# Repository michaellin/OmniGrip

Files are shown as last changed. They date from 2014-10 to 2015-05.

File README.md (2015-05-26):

## Description
The OmniGrip is a master manipulator gripper device capable of rendering a programmed stiffness. This open source project aims to add a seventh degree of freedom to the conventional Sensable Touch (Phantom Omni) haptic device. The project's files can be found at our [github repository](https://github.com/michaellin/OmniGrip). There are two versions of the device. The RE model uses a [Maxon RE-25 Motor](http://www.engr.ucsb.edu/~mdnip/me170c/datasheets/25mm_Motors.pdf) and the A-Max model uses a [Maxon A-Max-22 Motor](http://www.farnell.com/datasheets/484760.pdf). NOTE: the software currently only supports the RE model. It has not been tested for the A-Max model yet. For more details about the device refer to the conference paper: <link to future paper>.

## Assembly Instructions
List of materials needed to assemble the OmniGrip:

(quantity) description [McMaster-Carr part number]

1. (8) 3D printed parts of the device
  1. Long lever
  2. Short lever
  3. Frame center piece
  4. Frame top piece
  5. Frame bottom piece
  6. Long capstan gear
  7. Short capstan gear
  8. Handle
2. (6) Mini High-Precision Ball Bearing - ABEC-5                                                                [MC 57155K355]
3. (1) 10 Ft. Type 304 Stainless Steel Wire Rope, 7x19 Strand Core, 0.024" Dia, 70 Lb Break Strength, 10' Long  [MC 3461T621]
4. (2) Vented 18-8 Ss Socket Head Cap Screw, 4-40 Thread, 1/2" Length, .035" Vent Diameter                      [MC 93235A110]
5. (8) Type 316 Ss Socket Head Cap Screw, 0-80 Thread, 1/4" Long                                                [MC 92185A053]
6. (8) Brass Press-Fit Expansion Insert for Plastics without Flange, 0-80 Internal Thread, 1/8" Length          [MC 92395A109]
7. (2) Type 316 Stainless Steel Socket Head Cap Screw, 2-56 Thread, 1/4" Length                                 [MC 92185A077]
8. (2) Brass Press-Fit Expansion Insert for Plastics without Flange, 2-56 Internal Thread, 5/32" Length         [MC 92395A111]
9. (3) Metric 316 Stainless Steel Pan Head Phillips Machine Screw, M2 Size, 5mm Length, .4mm Pitch              [MC 90116A009]
10. (2) Copper Oval Compression Sleeve for 1/32" Rope Diameter, 1/4" Sleeve Length                              [MC 3897T31]

Important Note: most McMaster-Carr parts come in packs. The number specified in the parenthesis is just the amount of units used, not the number of packs you need to buy.

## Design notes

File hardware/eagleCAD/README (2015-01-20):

When using EagleCAD to open the Prototype layouts, some references might be broken initially. Relocate the files in "./lib/SparkFun-*". (* means wildcard/anything)

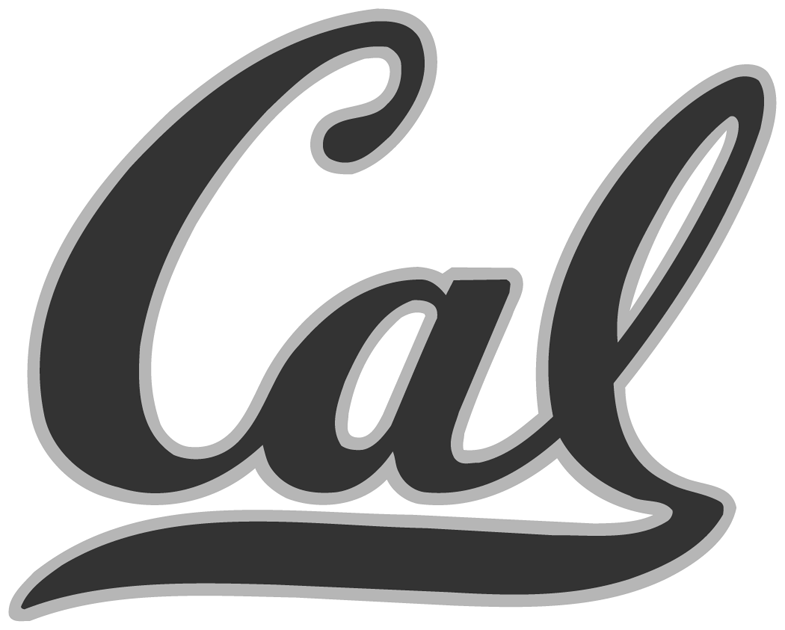
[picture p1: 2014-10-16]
hardware/eagleCAD/emblems/cal.bmp

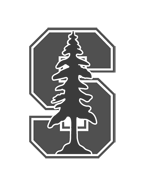
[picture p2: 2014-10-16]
hardware/eagleCAD/emblems/SU_BlockStree_2color copy.bmp

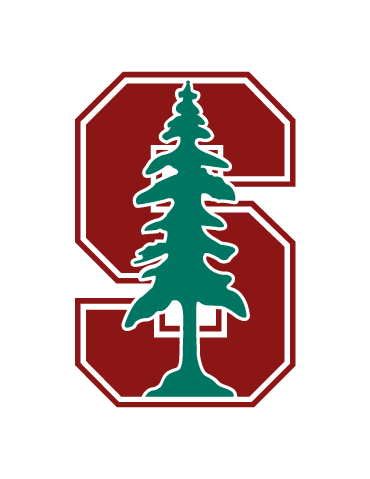
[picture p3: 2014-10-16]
hardware/eagleCAD/emblems/SU_BlockStree_2color.png

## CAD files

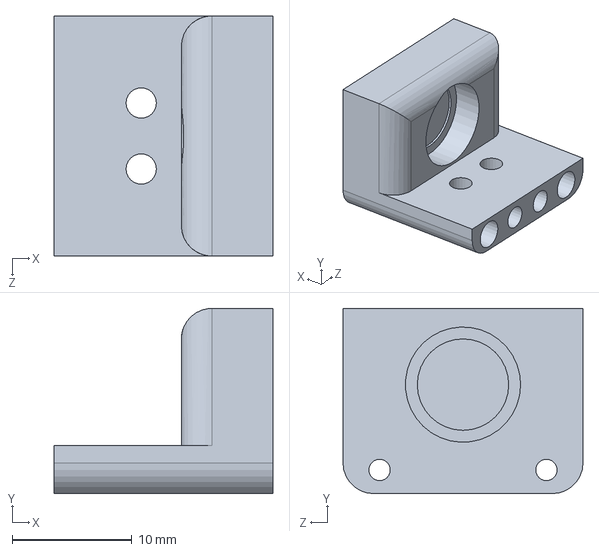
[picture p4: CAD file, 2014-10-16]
hardware/SolidWorksCAD/Model-AMAX-Motor/Center Piece RE 25.SLDPRT
18.2 x 15.4 x 20.0 mm

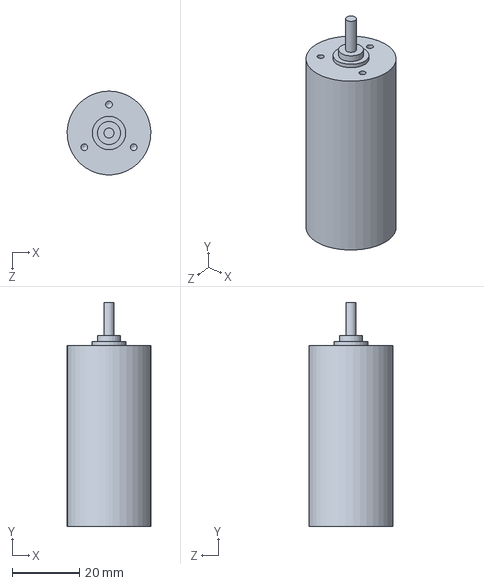
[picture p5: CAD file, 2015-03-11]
hardware/SolidWorksCAD/Model-RE-Motor/RE25 Motor.SLDPRT
25.0 x 66.8 x 25.0 mm

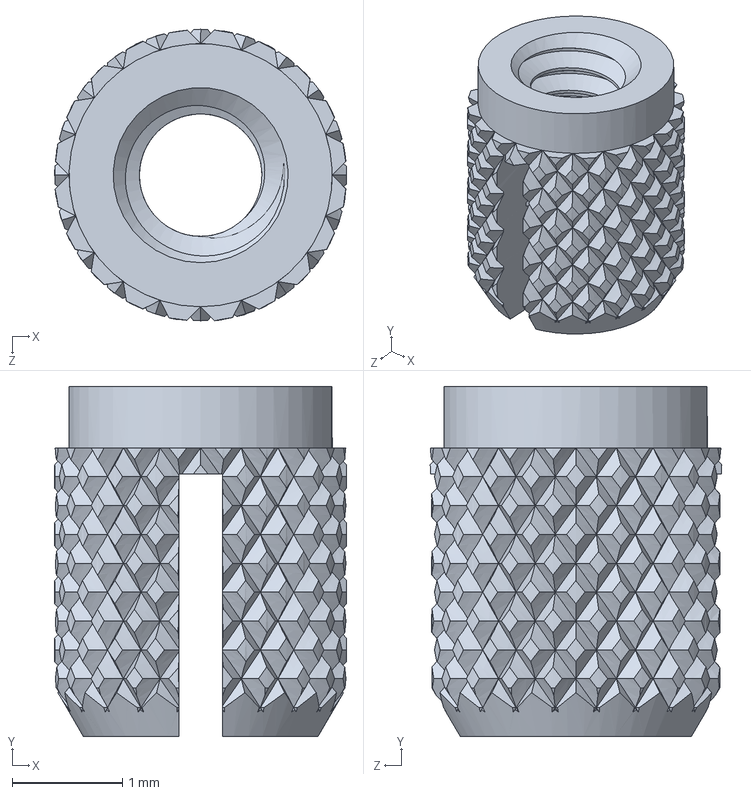
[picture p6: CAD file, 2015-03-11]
hardware/SolidWorksCAD/Model-RE-Motor/BrassInsert 0-80.SLDPRT
2.65 x 3.17 x 2.64 mm

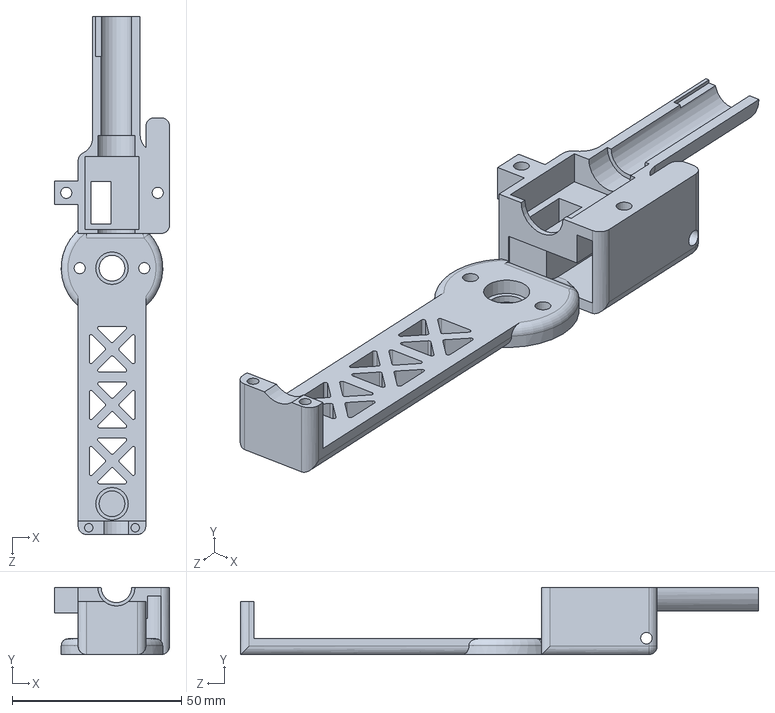
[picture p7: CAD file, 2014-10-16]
hardware/SolidWorksCAD/Model-AMAX-Motor/Top Piece Amax.SLDPRT
34.0 x 19.8 x 152.9 mm

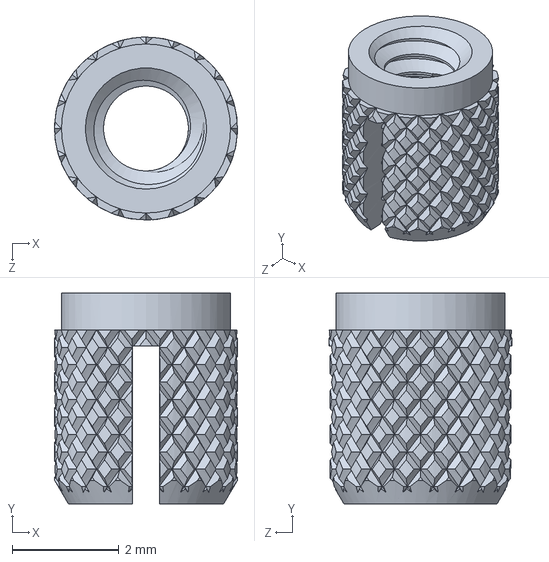
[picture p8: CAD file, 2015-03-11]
hardware/SolidWorksCAD/Model-RE-Motor/Brass Insert 2-56.SLDPRT
3.44 x 3.96 x 3.43 mm

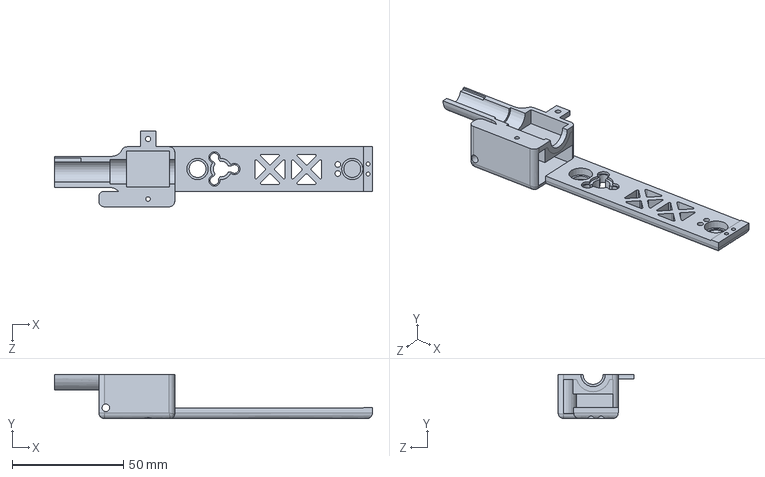
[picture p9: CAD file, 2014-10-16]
hardware/SolidWorksCAD/Model-AMAX-Motor/Bottom Piece Amax.SLDPRT
142.9 x 19.8 x 34.0 mm

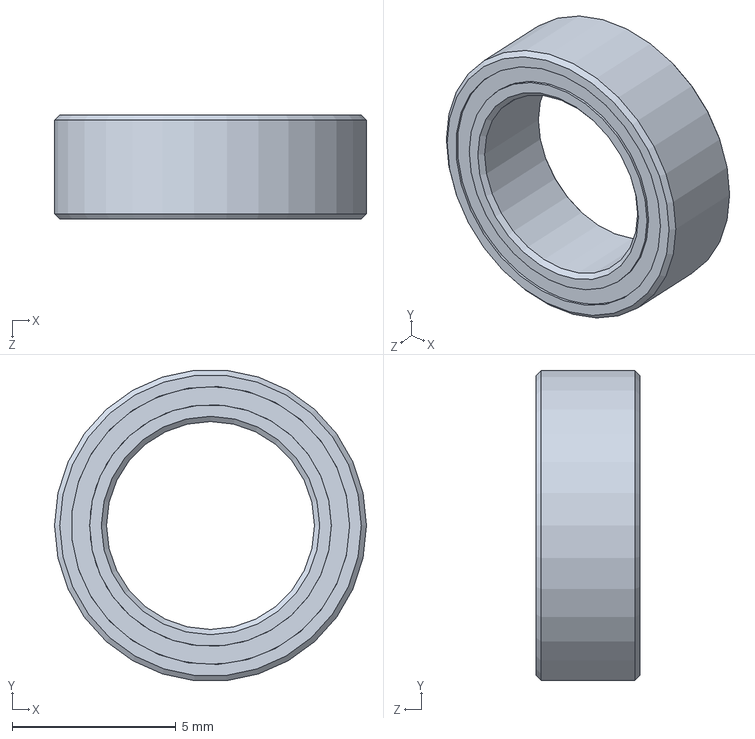
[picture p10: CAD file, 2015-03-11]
hardware/SolidWorksCAD/Model-RE-Motor/.25ID_.375OD_Bearing_60355K440.SLDPRT
9.53 x 9.47 x 3.17 mm

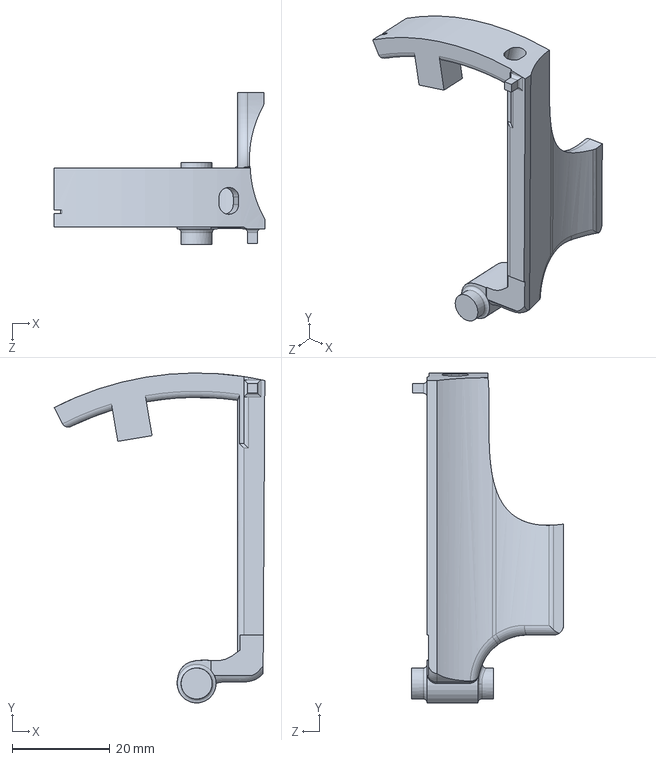
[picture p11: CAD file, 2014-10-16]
hardware/SolidWorksCAD/Model-AMAX-Motor/Long Lever Amax.SLDPRT
43.1 x 67.5 x 31.1 mm

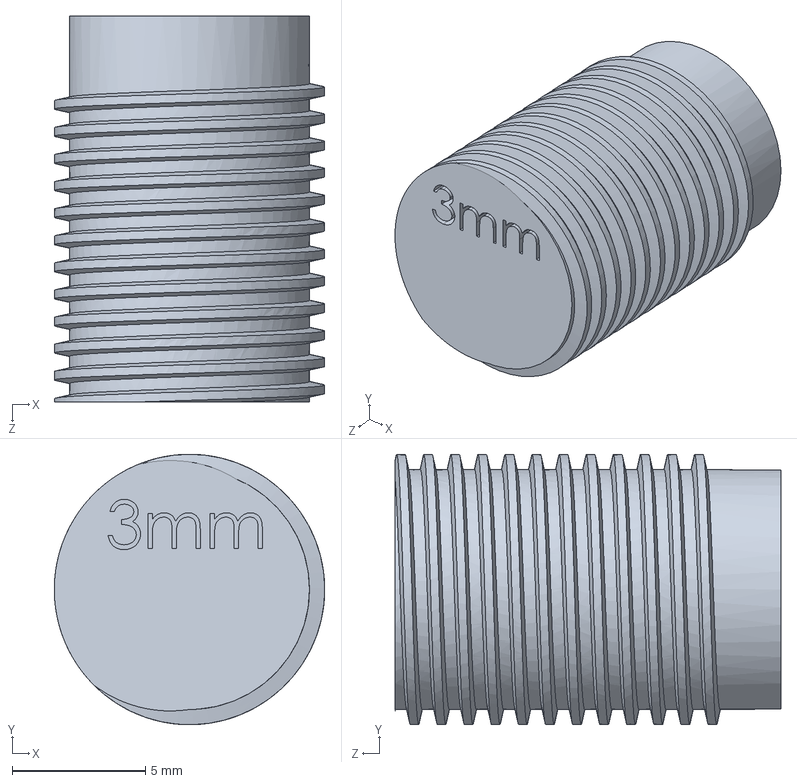
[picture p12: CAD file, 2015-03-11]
hardware/SolidWorksCAD/Model-RE-Motor/MIMA_capstan_h08in_d025in_3mm_RE 25.SLDPRT
10.1 x 10.1 x 14.5 mm

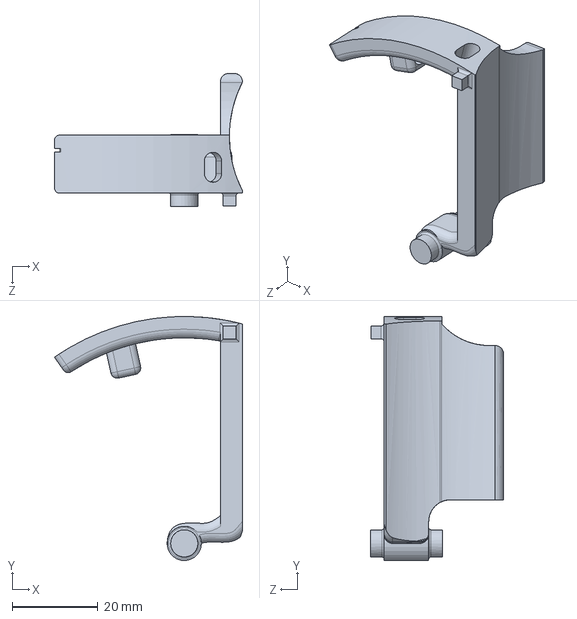
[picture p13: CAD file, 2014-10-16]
hardware/SolidWorksCAD/Model-AMAX-Motor/Short Lever Amax.SLDPRT
43.9 x 57.0 x 31.1 mm

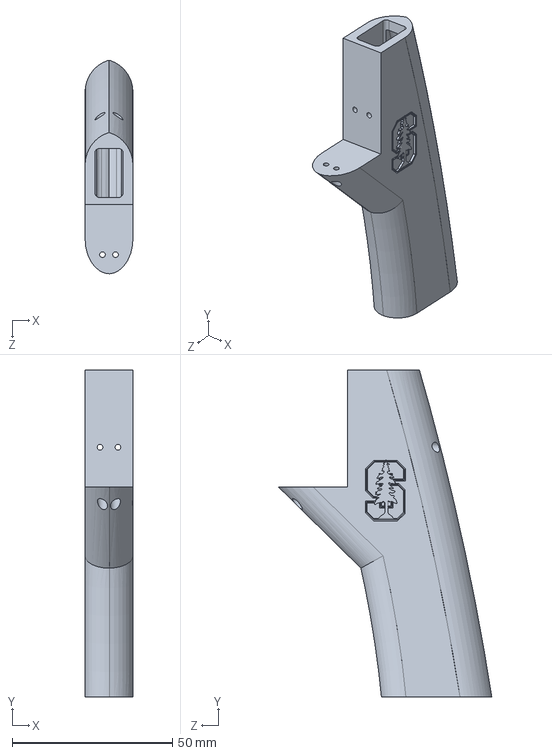
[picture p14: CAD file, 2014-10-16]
hardware/SolidWorksCAD/Model-AMAX-Motor/Handle Amax.SLDPRT
14.9 x 102.0 x 66.7 mm

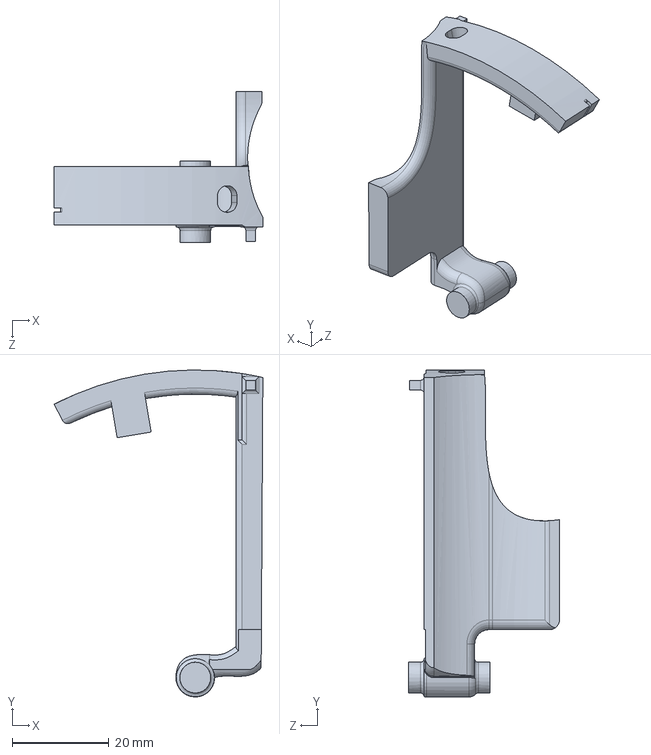
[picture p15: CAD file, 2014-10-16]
hardware/SolidWorksCAD/Model-RE-Motor/Long Lever RE 25.SLDPRT
43.1 x 67.5 x 31.1 mm

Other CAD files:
hardware/SolidWorksCAD/Model-AMAX-Motor/Center Piece Amax.SLDPRT
hardware/SolidWorksCAD/Model-RE-Motor/0-80_Brass Inserts_92395A109.SLDPRT
hardware/SolidWorksCAD/Model-RE-Motor/Top Piece RE 25.SLDPRT
hardware/SolidWorksCAD/Model-RE-Motor/Handle RE 25.SLDPRT
hardware/SolidWorksCAD/Model-RE-Motor/Bottom Piece RE 25.SLDPRT
hardware/SolidWorksCAD/Model-RE-Motor/Short Lever RE 25.SLDPRT
hardware/SolidWorksCAD/Model-RE-Motor/0-80 CapScrew .25''.SLDPRT
hardware/SolidWorksCAD/Model-RE-Motor/0-80_Socket_Cap_Screw_92200A055.SLDPRT
hardware/SolidWorksCAD/Model-RE-Motor/2-56 screw .25 length.SLDPRT
hardware/SolidWorksCAD/Model-RE-Motor/Bottom Piece RE 25.STL
hardware/SolidWorksCAD/Model-RE-Motor/M2 screw lg-5mm.SLDPRT
hardware/SolidWorksCAD/Model-RE-Motor/MIMA_capstan_h08in_d025in_Passive_Long.SLDPRT
hardware/SolidWorksCAD/Model-RE-Motor/Short Lever RE 25.STL

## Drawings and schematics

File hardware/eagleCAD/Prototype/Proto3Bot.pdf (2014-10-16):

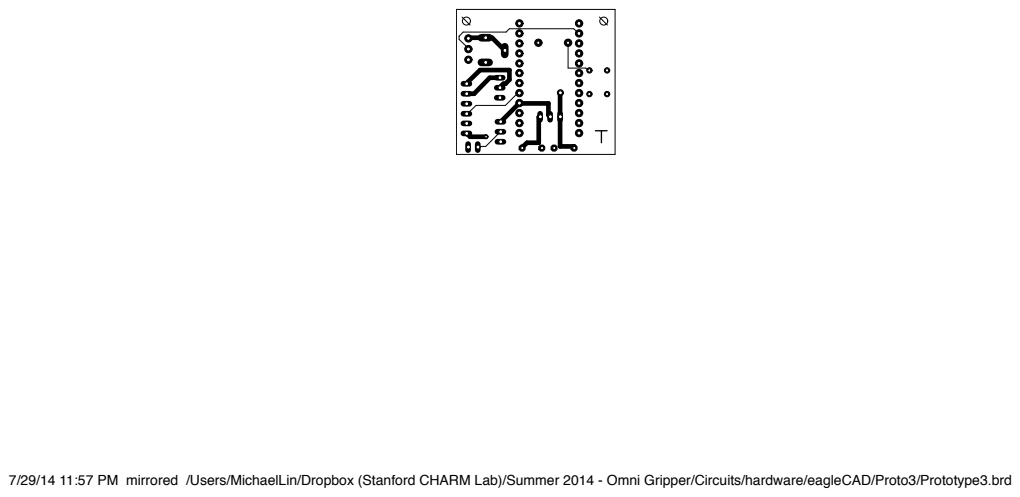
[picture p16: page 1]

7/29/14 11:57 PM mirrored /Users/MichaelLin/Dropbox (Stanford CHARM Lab)/Summer 2014 - Omni Gripper/Circuits/hardware/eagleCAD/Proto3/Prototype3.brd

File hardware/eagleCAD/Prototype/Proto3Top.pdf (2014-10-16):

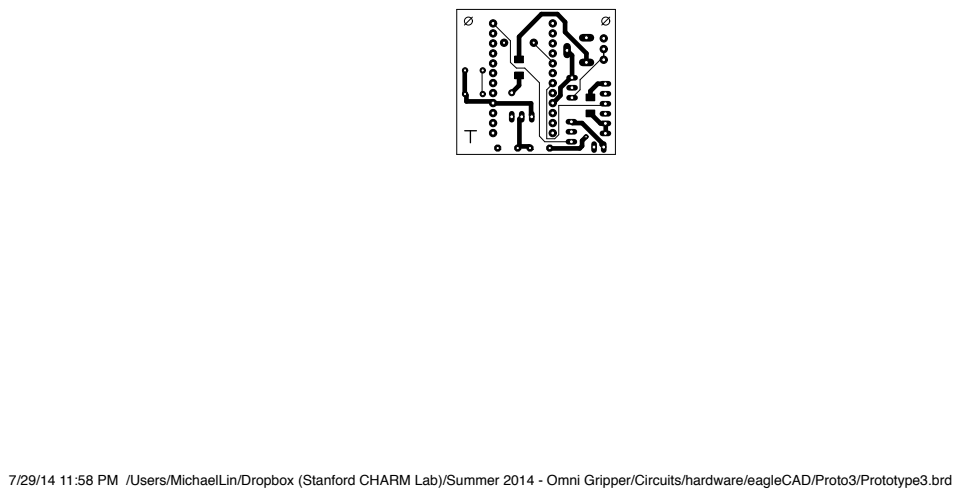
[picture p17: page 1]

7/29/14 11:58 PM /Users/MichaelLin/Dropbox (Stanford CHARM Lab)/Summer 2014 - Omni Gripper/Circuits/hardware/eagleCAD/Proto3/Prototype3.brd

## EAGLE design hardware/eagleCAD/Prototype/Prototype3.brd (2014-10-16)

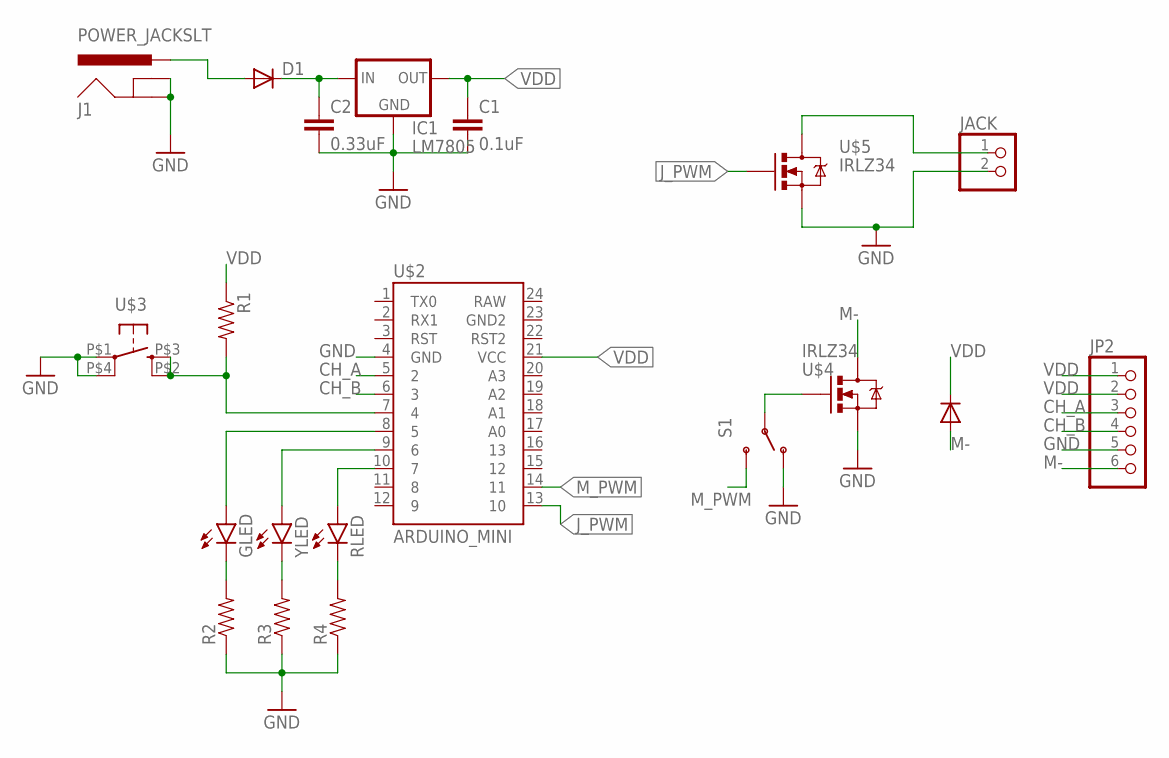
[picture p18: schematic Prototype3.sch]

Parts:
C1: 0.1uF; C5B2.5
C2: 0.33uF; C5B2.5
D1: SCHOTTKY-DIODE; SMD-DIODE
GLED: LED3MM
IC1: LM7805; TO-220(2)
J1: POWER_JACKSLT; POWER_JACK_SLOT
JACK: PINHD-1X2; 1X02
JP2: PINHD-1X6; 1X06
R1, R2, R3, R4: RESISTORAXIAL-0.3; AXIAL-0.3
RLED: LED3MM
S1: SWITCH-SPDTKIT; SWITCH-SPDT_KIT
U$1: SCHOTTKY-DIODE; SMD-DIODE
U$2: ARDUINO_MINI
U$3: PUSH-BUTTON; PUSHBTTN
U$4, U$5: IRLZ34; TO-220(2)
YLED: LED3MM

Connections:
CH_A: JP2.3, U$2.5 (2)
CH_B: JP2.4, U$2.6 (3)
GND: C1.2, C2.2, IC1.GND, J1.GND@1 (GNDBREAK), J1.GND@2 (GND), JACK.2, JP2.5, R2.P$1 (1), R3.P$1 (1), R4.P$1 (1), S1.1 (O), U$2.4 (GND), U$3.P$1 (1), U$3.P$4 (2), U$4.OUT (S), U$5.OUT (S)
J_PWM: U$2.13 (10), U$5.IN (G)
M-: JP2.6, U$1.P$1 (A), U$4.GND (D)
M_PWM: S1.3 (S), U$2.14 (11)
unnamed: JACK.1, U$5.GND (D)
unnamed: D1.P$1 (A), J1.PWR
unnamed: S1.2, U$4.IN (G)
unnamed: C2.1, D1.P$2 (C), IC1.IN
unnamed: R4.P$2 (2), RLED.K (C)
unnamed: R3.P$2 (2), YLED.K (C)
unnamed: GLED.K (C), R2.P$2 (2)
unnamed: GLED.A, U$2.8 (5)
unnamed: U$2.9 (6), YLED.A
unnamed: RLED.A, U$2.10 (7)
unnamed: R1.P$2 (2), U$2.7 (4), U$3.P$2 (4), U$3.P$3 (3)
VDD: C1.1, IC1.OUT, JP2.1, JP2.2, R1.P$1 (1), U$1.P$2 (C), U$2.21 (VCC)

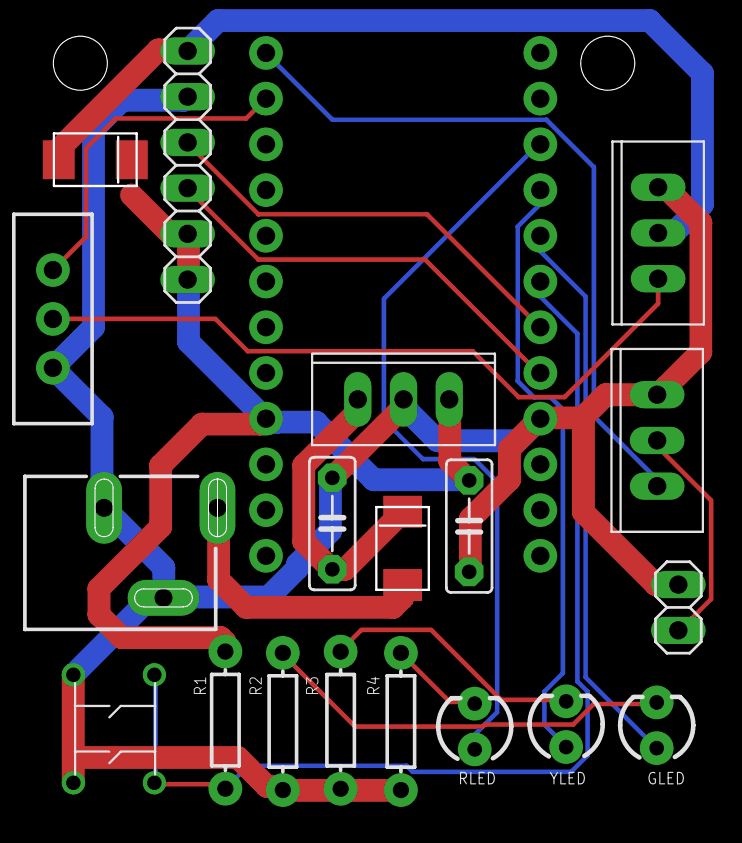
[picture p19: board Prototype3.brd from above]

Board: 2 copper layers, 20 parts (0 on the bottom side), 18 nets.

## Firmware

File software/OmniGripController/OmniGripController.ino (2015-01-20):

/* Motor controller
 * Encoder code from http://www.pjrc.com/teensy/td_libs_Encoder.html
 * Author: Michael Lin
 * PinOut for OmniGrip
 * Pin 2 and 3 -> Encoder pins ChA & ChB
 * Pin 4       -> Toggle Switch
 * Pin 5       -> Green LED
 * Pin 5       -> Yellow LED
 * Pin 6       -> Red LED
 */

#include <Encoder.h>
#include <math.h>

static const int   t1cntr = 31250;     //Max count for Timer1

/*Motor constants*/
static const float maxPWM = (1 << 8);  //Max PWM compare for Timer2
static const float maxOKPWM = maxPWM*0.42;  //Max Continuous current for RE25 is 1.5A and motor resistance is 2.7Ohm. So V=I*R -> maxOKPWM = 40%
static const float safePWM  = maxPWM*0.005; //PWM range safe enough to turn on the motor switch.

/*Audio Jack constants*/
static const float maxCmdGrip = t1cntr*0.8; // Dont want to command to Audio Jack more than 80% duty cycle to keep the waveform clean.

/*General constants*/
static const float maxGripEncCount = 1750; //Max encoder value when OmniGrip goes from fully open to fully closed


//static const float PWMOffset = 10; //Offset to overcome friction in grippers. Not used due to safety

//Conversions from encoder reading to desired PWM output
const float L_OmniGrip       = 55;                                 // in mm
const float encoder_range    = maxGripEncCount;                    //encoder count in a full swing
const float swing_range      = (25/encoder_range)*(M_PI/180);     // in rad
const float max_volts        = 12;                                 // in Volts
const float motor_resistance = 2.7;                                // in Ohms
const float K_torque         = 23.2;                               // in mNm/A for RE-25
const float capstan_radius   = 4.5;                                // in mm
const float L_daV            = 41;                                 // in mm da Vinci master constant(not used)
const float K_daV            = 5.4/L_daV;                          // in mN/rad da Vinci master constant(not used)

/** Conversion factor calculation
 *  I_eff = PWM*V_max/R_motor
 *  F_eff = I_eff*K_torque/capstan_radius
 *
 *  angle_reading_radian = input_encoder_reading*(25/encoder_range)*(pi/180)    25 is max swing in degrees
 *  F_des = K_stiff*angle_reading_radian/gripper_radius
 *
 *  F_eff = F_des
 *  (PWM*K_torque*V_max)/(R_motor*capstan_radius) = (encoder_reading*(25*pi/180)*K_stiff)/(encoder_range*gripper_radius)
 *  PWM, encoder_reading and K_stiff are variables. Eveything else is constant.
 */
 
//const float conv_factor = ((swing_range/encoder_range)*motor_resistance*capstan_radius*maxGripEncCount) / (L_OmniGrip*K_torque*max_volts);  //Conversion factor from encoder reading to commanded PWM in clock counter have to multiply by stiffness K
const float conv_factor = swing_range*(motor_resistance/(K_torque*max_volts))*(capstan_radius/L_OmniGrip)*maxPWM;  //Conversion factor from encoder reading to desired PWM duty cycle (in clock counter units i.e. multiply by maxPWM).

/*Pinouts*/
int GLED = 5;
int YLED = 6;
int RLED = 7;
int SWITCH = 4;

/*LPF constant*/
float alpha = 0.8;

/*Experiment Variables*/
const int totalStates = 3; //5 when testing stiffnesses
int conditionState    = 0;
int toggleSwitch      = 0; //State for switch. 1 if switch pressed. 0 otherwise.

//-----------CHANGE GAINS HERE----------
/*Array of different stiffness conditions. Mostly just need to change these.*/
//int K1[totalStates] = {40,  40,  55,  60,  80};
//int K2[totalStates] = {200, 230, 250, 270, 290};
//int K1[totalStates] = {40,  60,  75};
//int K2[totalStates] = {200, 250, 290};
int K1[totalStates] = {210, 280, 350};   //Safer set
int K2[totalStates] = {900, 1200, 1500}; //Safer set
//int K1[totalStates] = {240,  320,  400}; //Stiffer set
//int K2[totalStates] = {1050, 1400, 1750}; //Stiffer set

int force_offset = 6;   //In units of Timer counter (up to 256 for 100% PWM)
//--------------------------------

//Temporary variables
float temp1;
float prevPWM = 0;
float currPWM = 0;
float cmdPWM  = 0;
int currSwitchRead = 1;
int prevSwitchRead = 1; //Switch is HIGH when not pressed.
int LEDState;

// Change these two numbers to the pins connected to your encoder.
//   Best Performance: both pins have interrupt capability
Encoder myEnc(2, 3);

void setup() {
   pinMode(2, INPUT);                //Encoder ChA
   pinMode(3, INPUT);                //Encoder ChB
   
   pinMode(GLED, OUTPUT);            //Green LED
   pinMode(YLED, OUTPUT);            //Yellow LED
   pinMode(RLED, OUTPUT);            //Red LED
   
   pinMode(SWITCH, INPUT);           //Toggle Switch
   
   pinMode(10, OUTPUT);              //Drive PWM on digital pin 10 for Omni on Timer1 16-bit
   pinMode(11, OUTPUT);              //Drive PWM on digital pin 11 for Motor on Timer2 8-bit
   
   digitalWrite(11, LOW);            //Turn off this pin for safety
   
   /* Setup for Audio Jack Clock. This uses Timer 1 for sending PWM to pin 10.
    * The way this works is that there is an internal triangle waveform and a compare value OCR1B. Changing OCR1B changes the duty cycle
    * of the PWM output on Pin10 which drives the Audio Jack.*/
   TCCR1A = _BV(COM1A1)|_BV(COM1B1); //Setup Timer1 register TCCR1A for two compares COM1A1 and COM1B1
   TCCR1B = _BV(WGM13) | _BV(CS11);  //Setup Timer1 register TCCR1B with WGM13 for mode Phase and Freq correct, and CS11 for pre-scalar 16Mhz/8  
   ICR1 = t1cntr;                    //For 16Hz based on eq f=8Mhz/(2*N*ICR1) FOR ARDUINO MINI 8MHz
   
   /* This is the same as Audio Jack Clock but for the motor and it uses Timer2 instead.*/
   TCCR2A = 3 | _BV(COM2A1);         //Setup Timer2 register TCCR2A for two compares COM2A1 and COM2B1. TCCR2A = 3 is Fast PWM mode.
   TCCR2B = 1;                       //For 32KHz based on eq f=8Mhz/(256*N*ICR1) FOR ARDUINO MINI 8MHz where N is prescalar
   OCR2A = 0*maxPWM;                 //Initial PWM duty cycle for motor
   //Serial.begin(9600);
}

void loop() {
  
   /* Code for output to Audio Jack */
   long encoder_reading = myEnc.read();                        //Obtain current encoder reading
   //Serial.println(encoder_reading);
   //This should change to scale temp1 proportionally instead of capping at the bottom
   temp1 = float(encoder_reading*maxCmdGrip)/maxGripEncCount;  //Scale the encoder reading to a range corresponding to 15% to 80% for PWM on Audio Jack.
   if (int(temp1) < t1cntr*0.15) {
     OCR1B = t1cntr*0.15;                                      //Minimum PWM will be 15% duty cycle.
   } else {
     OCR1B = int(temp1);
   }
   
   /* Read toggle switch state */
   currSwitchRead = digitalRead(SWITCH);
   toggleSwitch   = switchPressed(currSwitchRead);
   //if (cmdPWM < safePWM && toggleSwitch == 1) {  //Fail-safe cmdPWM has to be low in order to allow change of stiffness
   if(toggleSwitch == 1) {
     conditionState += 1;
     if (conditionState == totalStates) { //Loop around every x amount of states
       conditionState = 0;
     }
     LEDState = conditionState;
   }
   LEDState = conditionState+1; //conditionState+1 since I want to toggle from 1 to 3
   
   /* Stiffness control */
   float spring_pos1 = 0;                           //Spring 1 start at position 0
   float kp1 = K1[conditionState];                  //Spring 1 stiffness coefficient in mNm/rad
   float spring_pos2 = maxGripEncCount*60/100;         //Spring 2  starts at 15 degrees (Max open an close is 25 degrees)
   float pos2_offset = maxGripEncCount*55/100;
   float kp2 = K2[conditionState];                  //Spring 2 stiffness coefficient in mNm/rad
   
   if (encoder_reading > spring_pos1) {
       cmdPWM = (kp1 * (encoder_reading-spring_pos1) * conv_factor);
   }
   if (encoder_reading > spring_pos2) {
       cmdPWM = (kp2 * (encoder_reading-pos2_offset) * conv_factor) + (kp1 * (encoder_reading-spring_pos1) * conv_factor);
   }
   cmdPWM += force_offset; //Adds the force offset
   
   //Serial.println(cmdPWM);
   if (encoder_reading > spring_pos1) {
     if (cmdPWM > maxOKPWM) {   //Cap the PWM so motors dont burn off
       LEDState = 6; //Force the motor at higher current and signal it with LED
     } else {
       OCR2A = cmdPWM;
       //Serial.println(cmdPWM);
     }
   } else {
     OCR2A = 0; //Fail-safe always turn off motor if encoder value is passed fully open.
   }
   
   if (cmdPWM < safePWM) { // For indicating safe zone in the motor.
     LEDState = 5;
   }
   updateLED(LEDState); //Update LED at the end
}

/**
 * Updates LEDs depending on the current condition
 */
void updateLED (int condition) {
  digitalWrite(GLED, LOW);
  digitalWrite(YLED, LOW);
  digitalWrite(RLED, LOW);
  
  if (condition == 1) {
    digitalWrite(GLED, HIGH);
  }
  if (condition == 2) {
    digitalWrite(YLED, HIGH);
  }
  if (condition == 3) {
    digitalWrite(RLED, HIGH);
  }
  if (condition == 4) {
      digitalWrite(GLED, HIGH);
      digitalWrite(YLED, HIGH);
  }
  if (condition == 5) {    //For indicating safe zone
      digitalWrite(GLED, HIGH);
      digitalWrite(RLED, HIGH);
  }
  if (condition == 6) {    //For indicating going over maxPWM
      digitalWrite(GLED, HIGH);
      digitalWrite(YLED, HIGH);
      digitalWrite(RLED, HIGH);
  }
}

int switchPressed (int currSwitchReading) {
  if (currSwitchReading == 1 && prevSwitchRead == 0) { //Rising edge of the switch
    prevSwitchRead = 1;
    return 1;  //Only return 1 in rising edge
  } else if (currSwitchReading == 0 && prevSwitchRead == 1) {
    prevSwitchRead = 0;
  }
  return 0;  
}

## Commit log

2014-10-16 Adding Solidworks parts
    [Prototype3.brd, Prototype3.sch]
2014-10-16 Re-adding hardware files
    [Bottom Piece Amax.SLDPRT, Bottom Piece RE 25.SLDPRT, Bottom Piece RE 25.STL, Center Piece Amax.SLDPRT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]
2015-01-20 adding materials list to readme
2015-03-11 fixing solidworks problems using pack and go.
    [.25ID_.375OD_Bearing_60355K440.SLDPRT, 0-80 CapScrew .25''.SLDPRT, 0-80_Brass Inserts_92395A109.SLDPRT, 0-80_Socket_Cap_Screw_92200A055.SLDPRT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]
2015-05-26 adding more to the materials list

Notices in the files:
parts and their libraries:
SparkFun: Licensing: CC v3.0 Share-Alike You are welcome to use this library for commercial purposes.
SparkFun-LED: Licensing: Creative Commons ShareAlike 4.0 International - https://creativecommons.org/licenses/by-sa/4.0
